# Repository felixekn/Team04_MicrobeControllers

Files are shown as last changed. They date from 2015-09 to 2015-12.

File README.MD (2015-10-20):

# Goal
A device capable of quickly measuring the OD600 of a culture tube

# Specifications
-  OD600 Range of 0.05-0.5
-  OD600 precision  of <0.02
-  Option: Functions with tubes with gradations
-  Tube to tube variability <0.02
-  Does not need to be portable, can utilize an outlet
-  Capable of measureing 1-100 samples in >15 minutes
-  Capable of being blanked against different media
-  Reads out at least 2 significant figures
-  Robust to rough handeling by user

# Checkpoints
-  Select a photodetector
-  Select a light source
-  Select splitter
-  Interface with photodetector
-  Intereface with light source
-  Determine performance parameters of system and if they meet our specifications
-  Design a user interaction method
-  Select parts for user interaction
-  Interface with parts for user interaction
-  Design chasis and wiring
-  Produce chasis and wiring
-  Code complete system
-  Analyze performance
  
#Project Title: 
**Rapid Optical Density Detector (RODD)**

#Rough Project Description
Develop a small optical density (OD) measuring device that can either sit in or near an incubator for the purpose of rapidly reading the OD600 of culture tubes containing bacteria to determine their growth phase.

#Project Abstract:
A ubiquitous synthetic biology protocol is to grow liquid cultures of cells in 14mL culture tubes within a large orbital shaker incubator to a desired optical density (OD) for various experimental reasons. The challenging and at times frustrating aspect of this protocol is quantifying when the cells have reached their desired density. Traditionally, researchers either pipette samples into cuvettes and read these on a large spectrophotometer or hold each culture tube up to a light source and estimate OD based on experience. The first approach does not scale well with increasing culture tubes while the latter approach is susceptible to large errors especially at low ODs (<0.1 OD 600nm). A solution to this problem is to develop a device that sits within or on the orbital incubator that can read the OD of liquid cultures while they're within their culture tubes. By using Beer's law, an Arduino, a couple of photo detectors, and a laser, the proposed OD measuring device will be able to accurately (+/- 0.1 OD 600nm) and rapidly read out culture tube OD for the purpose of quickly quantifying if a liquid cell culture has reached its desired OD.

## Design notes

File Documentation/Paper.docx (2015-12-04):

A Low Cost Culture Tube Spectrophotometer

BIOE521 - 12/3/2015 - Felix Ekness, Brian Landry

Abstract

A ubiquitous synthetic biology protocol is to grow liquid cultures of cells in 14mL culture tubes within a large orbital shaker incubator to a desired optical density (OD) for various experimental reasons. The challenging and at times frustrating aspect of this protocol is quantifying when the cells have reached their desired density. Traditionally, researchers either pipette samples into cuvettes and read these on a expensive spectrophotometer or hold each culture tube up to a light source and estimate OD based on experience. The first approach is expensive and does not scale well with increasing culture tubes while the latter approach is susceptible to large errors especially at low ODs (<0.1 OD 600nm). We have solved this problem with the development of a compact and cheap spectrophotometer named the Rapid Optical Density Detector (RODD) that can measure OD through the culture tubes. RODD uses the Beer-Lambert law, an Arduino Uno, a single light-to-frequency converter, and a 600nm LED, a four segment LED display, a push button, and a 3D printed enclosure to cheaply and rapidly measure the OD of liquid cultures within 14mL culture tubes with a resolution of +/- 0.01 OD.

Background and Significance

In synthetic biology laboratories, measuring and tracking the density of cells within liquid cultures is paramount to nearly all in vivo experiments. As bacteria grow in liquid media, they consume nutrients and increase in density. During growth, the available nutrients decrease, resulting in phenotypic changes that affect experimental outputs. Thus it is crucial for experiments to end at the same cell density to avoid phenotypic changes, such as variations in DNA replication speed. To measure cell density within standard 14mL liquid culture tubes, two techniques are used: measuring the absorbance of the culture using a spectrophotometer or measuring absorbance through eyeballing.

Spectrophotometers measure the absorbance of a 600nm laser through a 1cm path of the liquid culture. This measurement is known as the optical density (OD) at 600nm (OD600) and is a standard proxy for microbial cell density. Spectrophotometers have been around for decades and although they are ubiquitous in laboratories, they are costly to purchase ($500-2000 used on Ebay and >$5000 new from VWR [1,2]), bulky, and require samples be placed into expensive ($1/per), non reusable cuvettes. Their high cost limits labs to usually one spectrophotometer and the requirement of pipetting samples into cuvettes becomes financially and time costly for >10 samples as well as perturbs the growth of the liquid cultures being measured. While there have been attempts to make cheap spectrophotometers, they have been impractical for laboratory environments or use the same time intensive and costly cuvettes [3,4].

The other technique of measuring liquid culture OD is through eyeballing the liquid culture within its culture tube against a light source. This technique requires experience but is cheap, quick, and does not perturb the growth environment of the cultures. Measuring OD with this method is prefered for >10 samples but is known to be highly inaccurate even for the most experienced researcher. Thus a cheap, quick to use, and accurate spectrophotometer is needed to enable synthetic biologists to rapidly and precisely measure OD of large quantities of experimental liquid culture tubes without perturbing the growth environment of the cells.

Design and Development

Below are the specifications for our spectrophotometer named Rapid Optical Density Detector (RODD):

Property | Specification | Achieved Value
Measurement Range | 0.05-0.5 OD600 | 0.05-1.0 OD600
Precision | <0.02 OD600 | +/- 0.01 OD600
Portability | Can be located next to an incubator but can still use a wall outlet for power | Achieved specification
Measurement rate | > 10 Samples/minute | 30 samples/minute
Visual Readout | Contains at least 2 significant figures | Contains 3 significant figures and a sign
Durability | Capable of being roughly handled and occasionally dropped | Survived testing and simulated dropping
Ease of use | Requires minimal interaction and promotes quick use | A single button press activates the machine which then has continual readout to the user
Cost | <$50 | Button = $0.5 Arduino Uno = $24.95 600nm LED = $0.35 Light-to-frequency-converter = $3.56 LED Display = $16.95 3D printed Housing = negligible Total = $46.31

User interface design

We approached our user interface with the goal of it being simple and quick to use. This meant limiting user interaction and achieving quick feedback to the user of the predicted OD600 of the culture. We first specified the four usage modes of the device:

1. Turned on
2. Measuring the blank
3. Measuring a sample
4. Turned off

Our first design decision was to condense the user input required to transition from the 4th state to the 1st and then 2nd states to a single button press, which both turns on the device, activating the numeric display, as well as initiates the blanking procedure. To further simplify usage we then automated transition from measuring the blank to measuring a sample to occur after one second of measuring the blank. While the device is measuring the sample it displays a one second running average of the OD600 reading. This real time display speeds up feedback to the user of the measured OD600 of the culture, decreasing the time required to quantify the density of the culture. It additionally removes the need for the user to signal the RODD each time a new sample is being measured, instead the user simply inserts the new sample and waits for the reading to stabilize after one second. Lastly, we created an automated turn off of the RODD after 10 minutes, both negating the need for the user to turn it off as well as removing the possibility of it accidentally being left on for long periods of time. A summary of the designed workflow is depicted in the flowchart below.

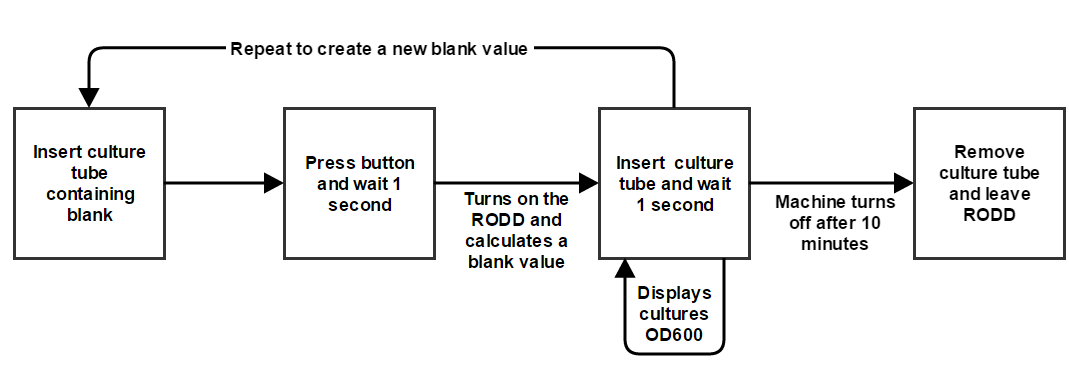
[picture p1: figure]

Figure 1: RODD user workflow flowchart

Spectrophotometer part selection

Part selection for RODD focused on attaining a high signal to noise ratio with relatively cheap parts. This lead to initially choosing a light-to-frequency-converter (LTFC) (part TSL237) that linearly converts input light intensity to an output square wave frequency over 5 logs of light intensity and an economical red laser (VLM-635/650-03 Series) with a wavelength of 635-650nm and beam diameter of 6+/-1 mm. After wiring these to an Arduino Uno and placing them within our custom 3D printed housing (see Figure 2A), it was observed that slight tilting of the culture tube dramatically changed the output of the LTFC. This was due to the laser’s focused beam and how the beam traveled through the culture tube. A slight change in the angle of entry into the culture tube resulted in a refraction large enough to shift the focus of the beam away from the center of the LTFC. This resulted in large OD600 variability from tube to tube which caused the noise of the system to surpass the signal. To fix this issue, the laser was swapped out for a less powerful but wider beam diameter LED. Since the LED’s beam diameter entering the culture tube is much larger than the laser’s, the effect of the refraction was predicted to be much less since the main focus of the LED beam should still hit the LTFC after refraction (see Figure 2B). Upon testing this hypothesis, the signal to noise ration was greatly increased with the LED OD600 light source configuration and thus RODD uses an LED instead of laser OD600 light source.

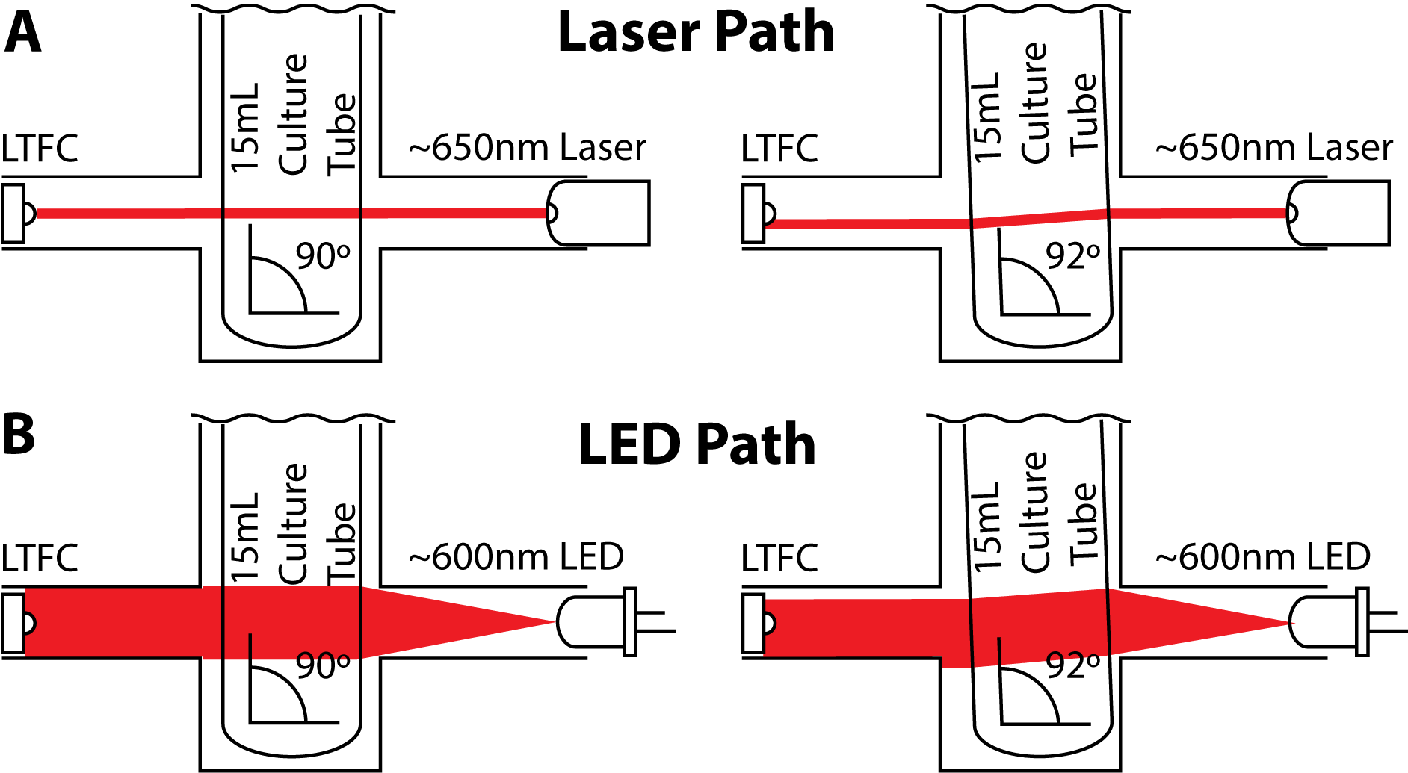
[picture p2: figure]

Figure 2: Beam path deviation of OD light source due to refraction when culture tube is tilted by 2º

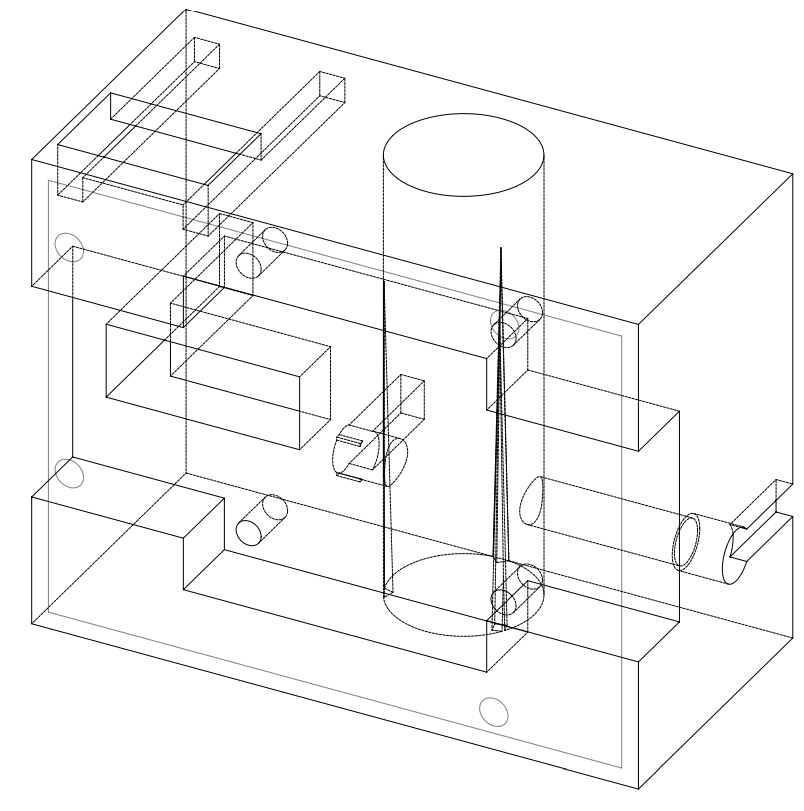
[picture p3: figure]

Design of casing

Figure 3: Diagram of the custom 3D printed housing that RODD uses.

When considering the selection of materials and organization of the physical parts of the RODD we took into expected levels of handling, our prior knowledge as well as the various fabrication technologies we had access to. We choose to 3D print over technologies such as laser cutting to create the casing for the RODD because it enabled the creation of various enclosed wiring paths. This resulted in compartmentalized wiring hidden from the user which we hope will make the connections more durable. We also had previous experience creating and printing models and had access to a 3D printer in our lab. The final model which was printed is shown below.

During testing of prototypes of our device we found that the angle of the culture tube greatly influenced measured absorbance, particularly when used with a laser (see Figure 2). Although the light source was changed to an LED to fix this issue, we also redesigned the culture tube holder to have a tighter fit. We used three triangular protrusions placed on the sides of the tube holder which decreased the relative diameter of the holder from the entry to the bottom of the holder (Figure 3). These protrusions in addition to the use of an LED light source eliminated previously identified noise generated from the vertical angle of the culture tube within its holder.

Coding

The RODD was programmed in the Arduino Programming Language using the standard arduino sketch format. The core of the program is contained in a loop which updates the state of the device at a set interval. The loop checks for changes in the state of the button, and then begins countdowns to both end the blanking of the device (measures light intensity through a culture with no cells which is a proxy for input light source) after one second and operation of the device after 10 minutes. It then records experimental measurements from the LTFC, computes the OD600 through the Beer-Lambert law, and displays the computed output on a four segment LED screen.

An important feature of this design was to create a responsive system while also supporting continuous integration from the synchronous photodetector. The original design queried the photodetector for a measurement over a one second time period. However, this locked the system for the entire second, making both the button and LED unresponsive during this period. To accommodate this while still calculating a one second average from the photodetector we created a continuously updated buffer which stored the last ten measurements from the photodetector. The LTFC was then queried ten times a second for a 100 millisecond period and these values were stored in the buffer. This permitted updates of the LED and button state every 100ms creating a much more responsive system. Additionally, it enabled the display of a continuously updating one second running average OD600 value to the user.

Quantification and Qualification

Calibration Technique

RODD was calibrated to display OD600 using 10 serially diluted titanium dioxide colloid solutions (suspended in water). These solutions were first read on our lab’s commercial spectrophotometer within 1mL cuvettes (Table 2, column 1). Then these solutions were measured within 14mL culture tubes at a volume of 4mL within RODD (Table 2, column 2). With both of these measurements, a first order polynomial was fitted to the spectrophotometer and RODD readings to create a mapping between spectrophotometer OD600 and RODD absorbance. This mapping was then hard coded into the core code that calculates RODD OD. The standard titanium dioxide solutions were then remeasured with the now calibrated RODD, yielding OD600 values +/-0.01 away from the spectrophotometer OD600 measurements of the same standard solutions (Table 2, column 3).

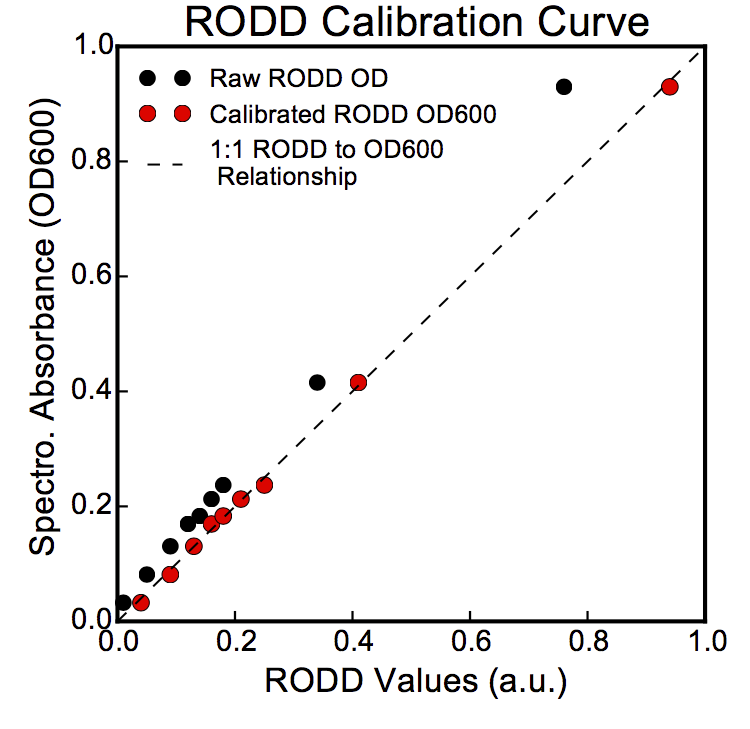
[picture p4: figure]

Spectrophotometer OD600 | Raw RODD OD | Calibrated RODD OD600
0.0325 | 0.01 | 0.04
0.08145 | 0.05 | 0.09
0.13062 | 0.09 | 0.13
0.16941 | 0.12 | 0.16
0.18323 | 0.14 | 0.18
0.21266 | 0.16 | 0.21
0.23708 | 0.18 | 0.25
0.41538 | 0.34 | 0.41
0.92972 | 0.76 | 0.94

Table 2: Spectrophotometer and RODD OD readings of 10 serially diluted titanium dioxide colloid solutions.

Figure 4: Plot of the values located in Table 2. The 1:1 RODD to OD600 relationship is the ideal relationship between the OD600 values RODD reads and what the spectrophotometer outputs

Deployment

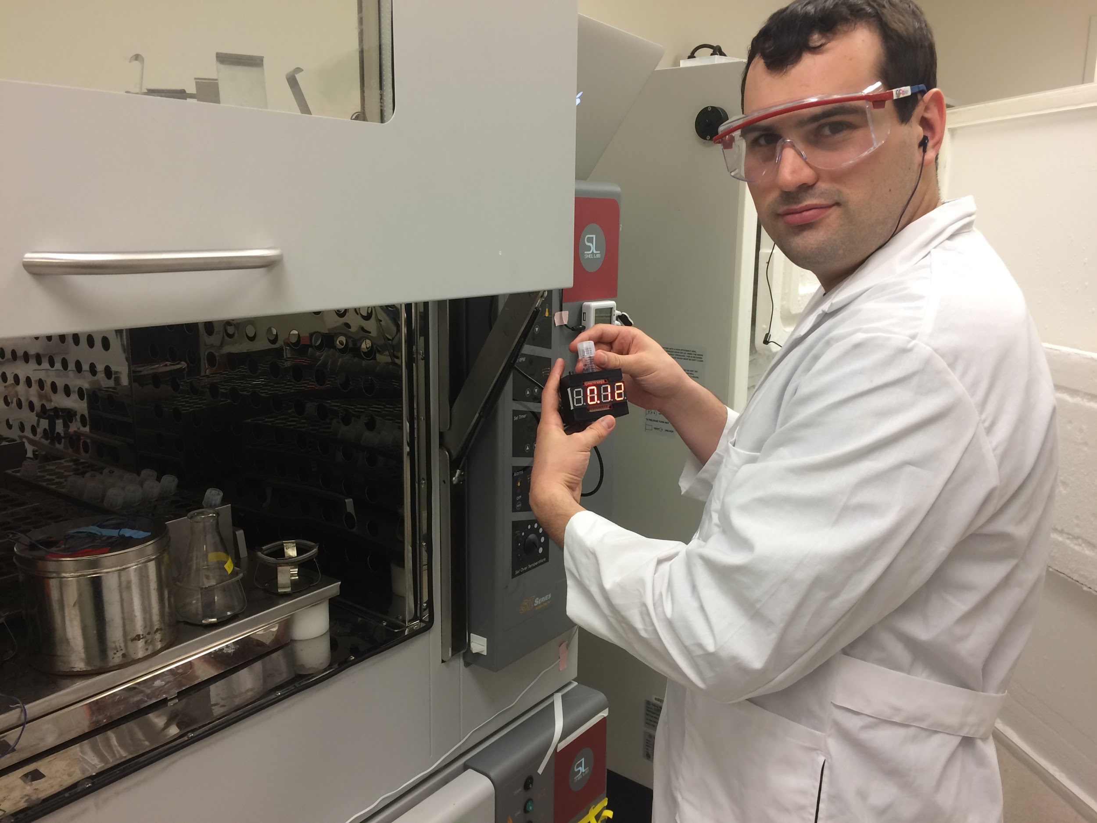
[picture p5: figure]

The extensive prototyping accomplished in this project has led to a device that is ready for preliminary deployment in our lab environment. We have begun to use the RODD to measure the OD600 of cultures in our incubator in the Tabor Lab (see image below). However there are several additional improvements which we are interested in examining. Primarily we would like to extend our 3D enclosure to cover the Arduino in addition to our electrical components. We expect this will increase the hardiness of the RODD and lead to a better user experiences. We are also interested in adding a web based storage system for the OD600 measurements from the device. We envision a system where the user presses the button after inserting each culture, which records the current reading to a spreadsheet that can subsequently be access via the internet. We look forward to adding these improvements to the RODD and demonstrating its long term performance in the Tabor Lab.

Figure 5: RODD in action

Citations

[1] Ebay. Search Term: “Spectrophotometer.” http://www.ebay.com/bhp/spectrophotometer

[2] VWR. Product Category: “Spectrometers.”

https://us.vwr.com/store/search?label=&vpc=&pimId=597202

[3] D. R. Albert, M. A. Todt, H. F. Davis. “A Low-Cost Quantitative Absorption

Spectrophotometer.” J. Chem. Educ. 2012, 89, 1432-1435.

[4] Dusjagr. “Optical Density Sensor aka Kafi-Schnapps Detektor.” Makerbot Thingiverse. Apr

15, 2013. http://www.thingiverse.com/thing:74415

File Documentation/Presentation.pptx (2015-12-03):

## The RODD: A Low Cost Culture Tube Spectrophotometer

- Brian Landry, Felix Ekness

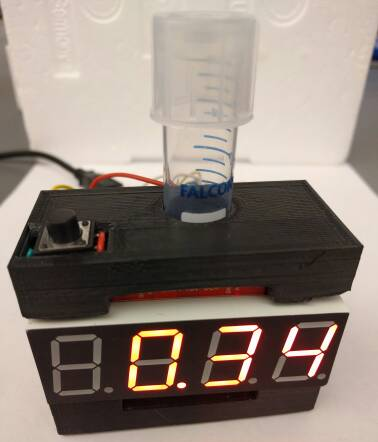
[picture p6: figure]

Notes: Felix

## Counting Bacteria in a Culture Tube

- Cannot monitor density of bacteria in standard culture tube
  - Volume required to use spectrophotometer is too much
  - Tube doesn’t work with spectrophotometer

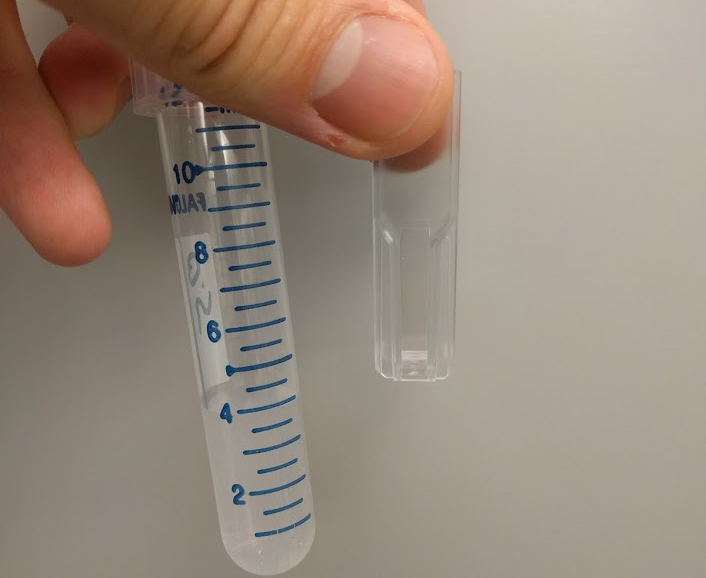
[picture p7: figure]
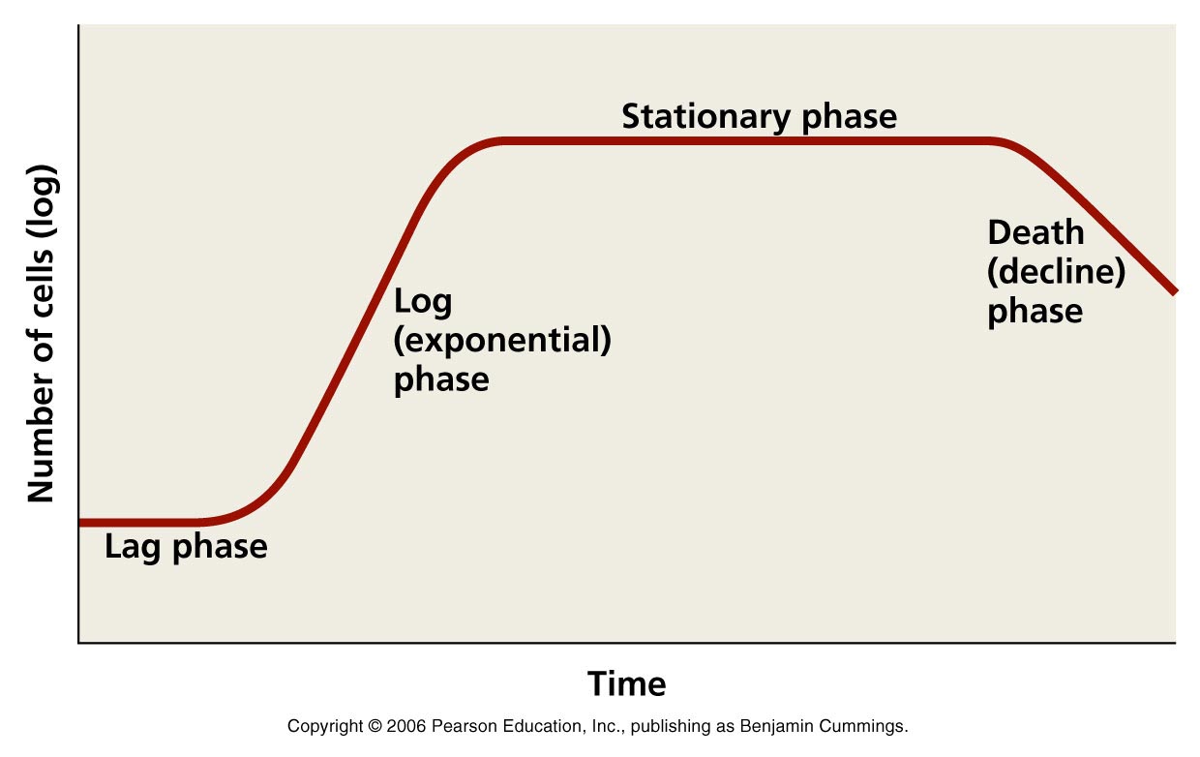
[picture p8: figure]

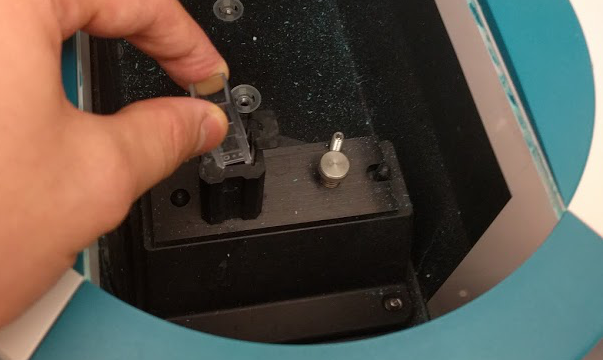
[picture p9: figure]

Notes: Felix

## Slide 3

Counting Bacteria in a Culture Tube

- Cannot monitor density of bacteria in standard culture tube
  - Volume required to use spectrophotometer is too much
  - Tube doesn’t work with spectrophotometer

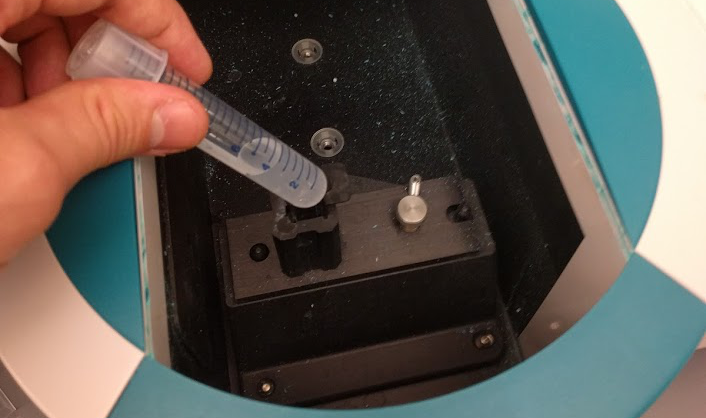
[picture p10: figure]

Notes: Felix

## Proposed Solution: The RODD

- A Rapid Optical Density Detector (RODD)
- A mini spectrophotometer which will sit next to a lab incubator to monitor many bacterial cultures simultaneously
- Should be easy, quick and intuitive to use
- Needs to be precise enough to allow us to experiment on bacteria in correct growth range

Property | Specification
Measurement Range | 0.05-0.5 OD600
Precision | <0.02 OD600
Portability | Can be located next to an incubator but can still use a wall outlet for power
Measurement rate | > 10 Samples/minute
Visual Readout | Contains at least 2 significant figures
Durability | Capable of being roughly handled and occasionally dropped
Ease of use | Requires minimal interaction and promotes quick use
Cost | <$50

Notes: Felix

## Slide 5

Property | Specification
Portability | Can be located next to an incubator but can still use a wall outlet for power
Measurement rate | > 10 Samples/minute
Visual Readout | Contains at least 2 significant figures
Durability | Capable of being roughly handled and occasionally dropped
Ease of use | Requires minimal interaction and promotes quick use

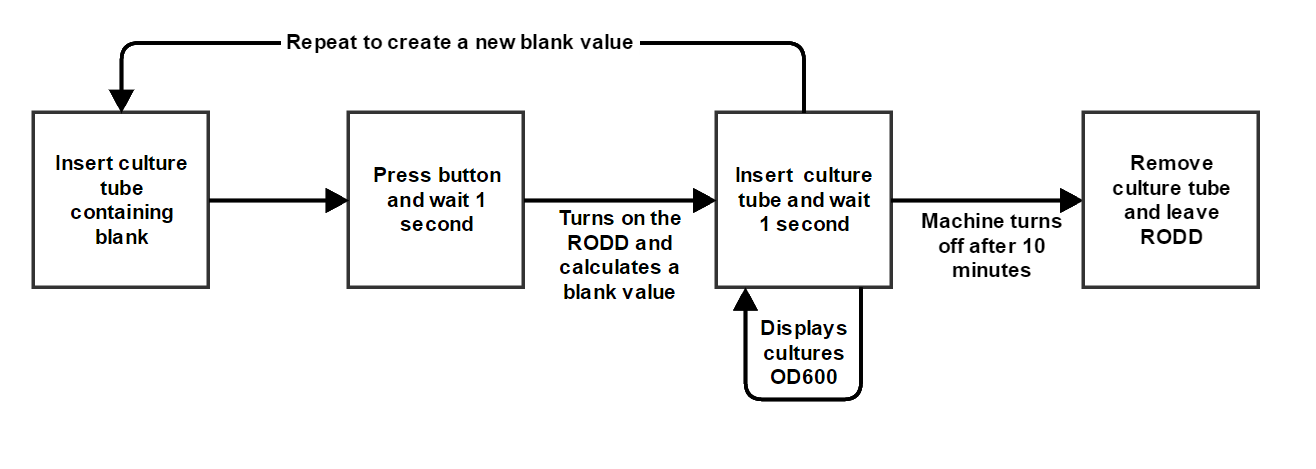
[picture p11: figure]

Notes: Brian

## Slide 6

Photodetector: large linear range to provide high precision and accuracy

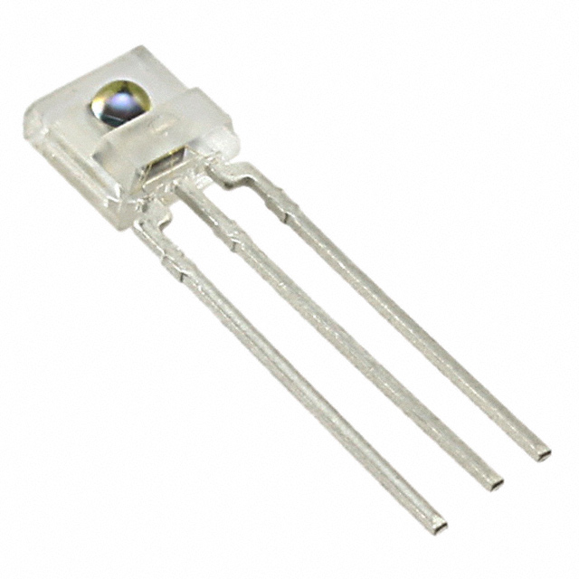
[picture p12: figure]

650nm laser for a bright concentrated light source

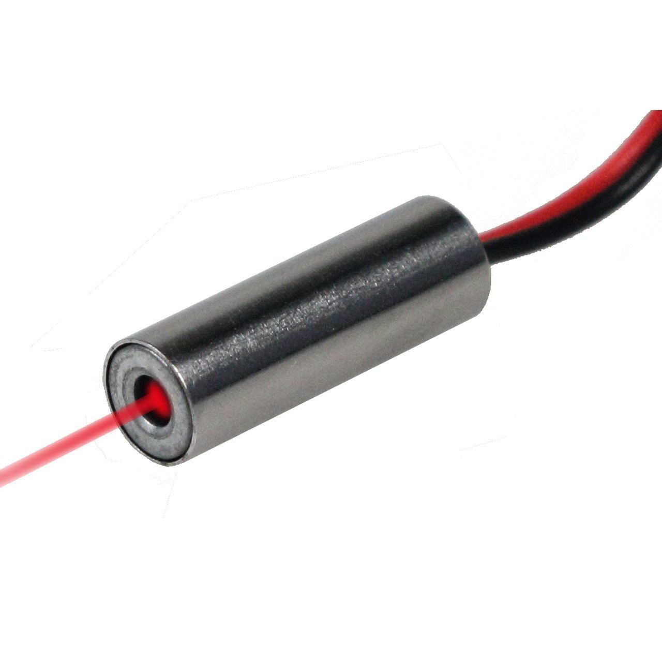
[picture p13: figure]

Single large button for user input

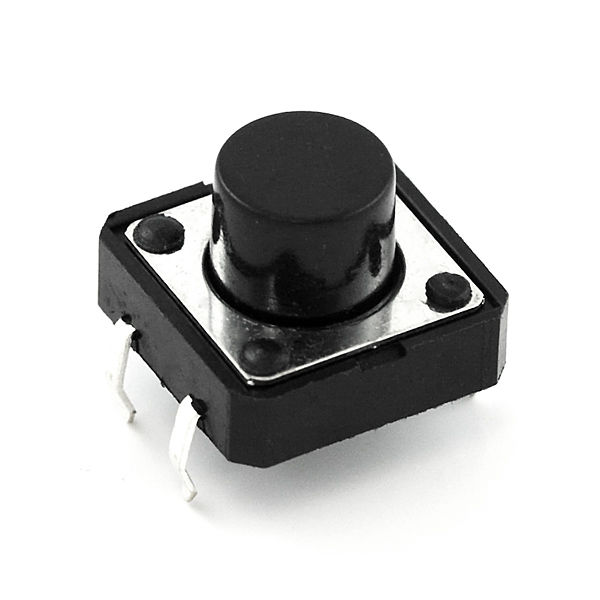
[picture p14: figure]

Four digit seven segment display capable of displaying three signed digits

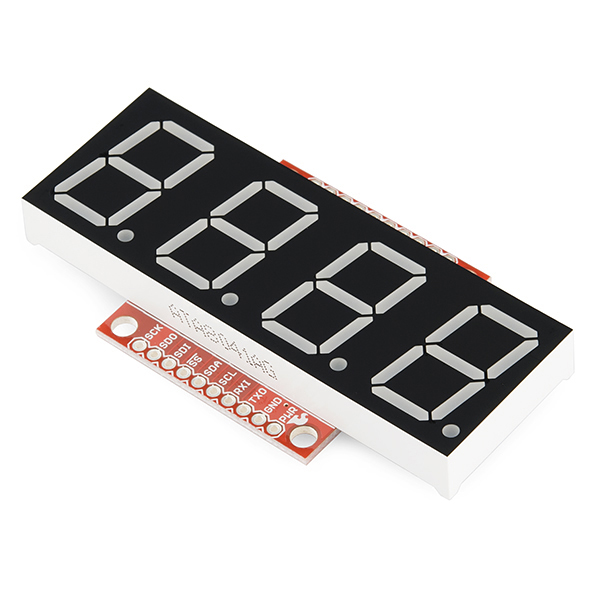
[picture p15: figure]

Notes: Brian

## Construction of the RODD

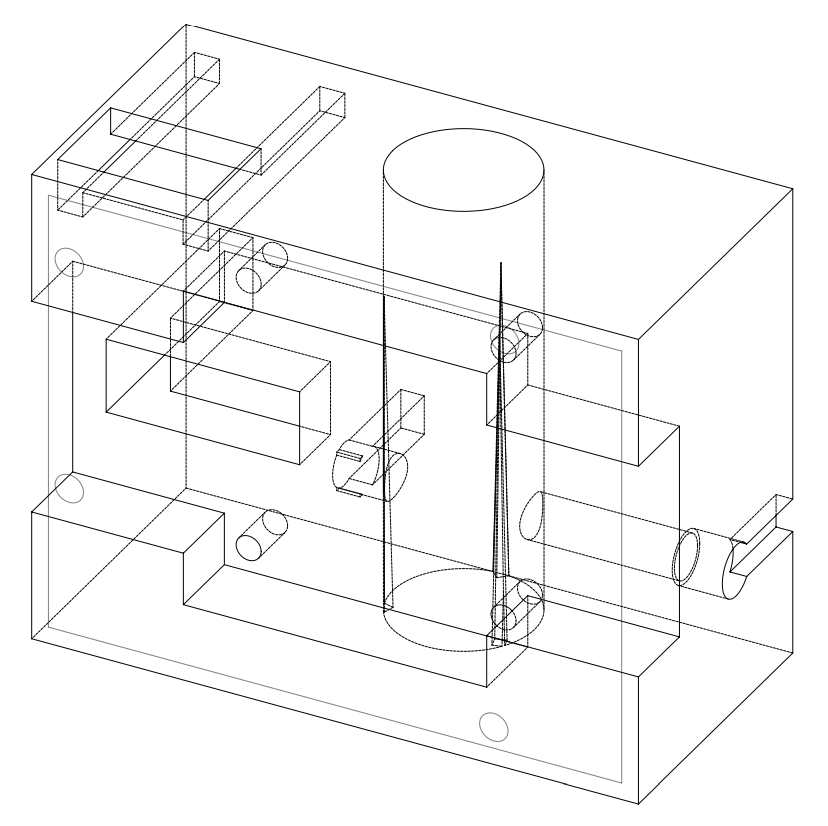
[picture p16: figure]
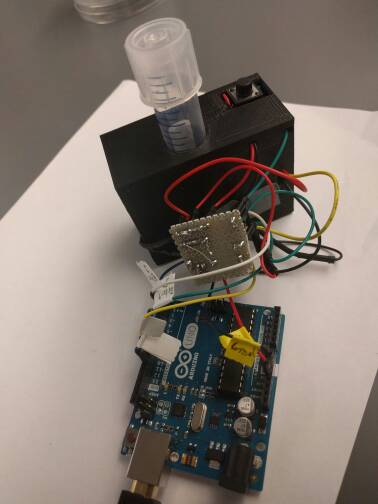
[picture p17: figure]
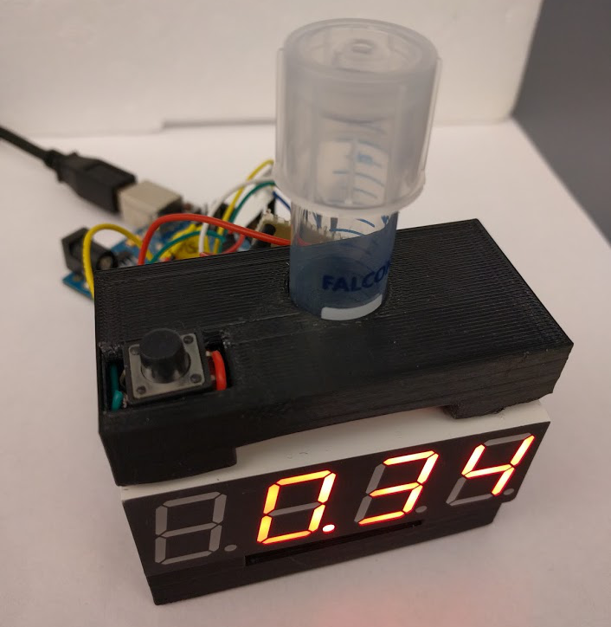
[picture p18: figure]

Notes: Brian

## Engineering Challenge: A responsive program

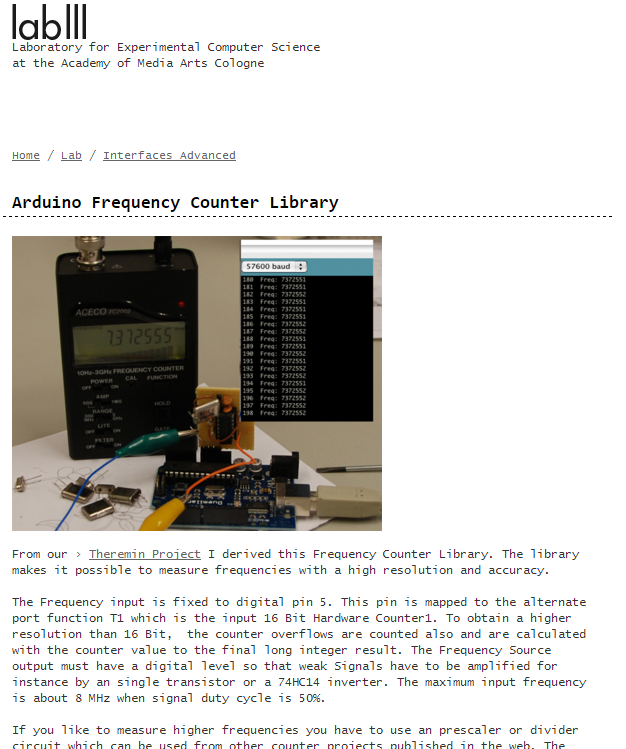
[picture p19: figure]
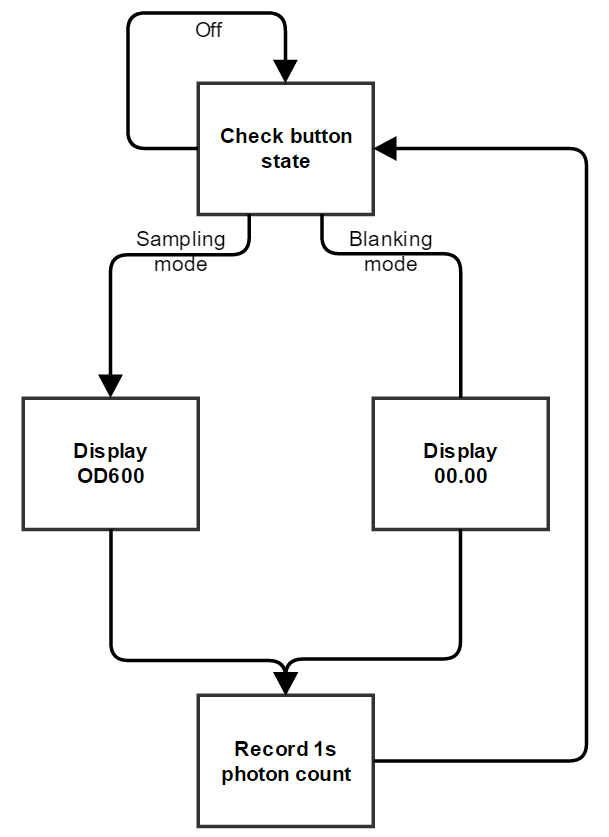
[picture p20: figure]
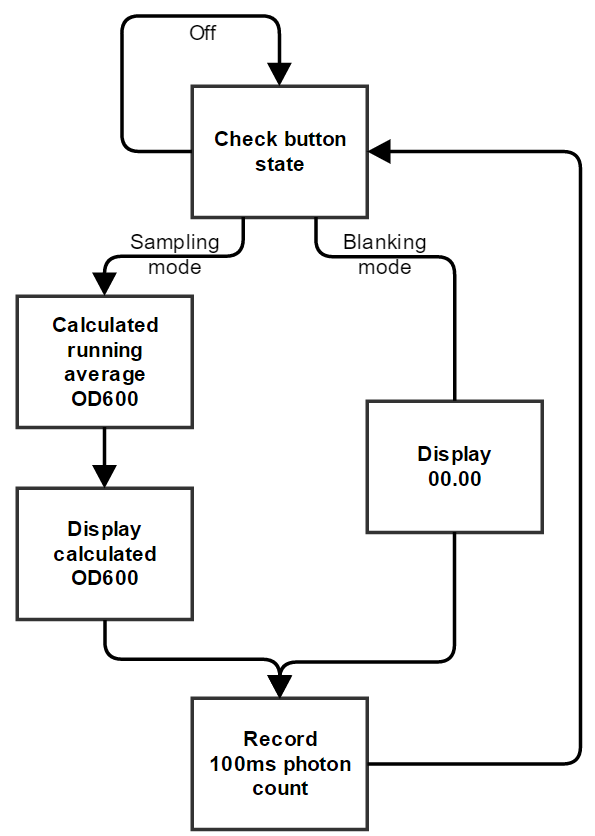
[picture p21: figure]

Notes: Brian

## Engineering Challenge: A responsive program

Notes: Brian

## Engineering Challenge: Laser deflection

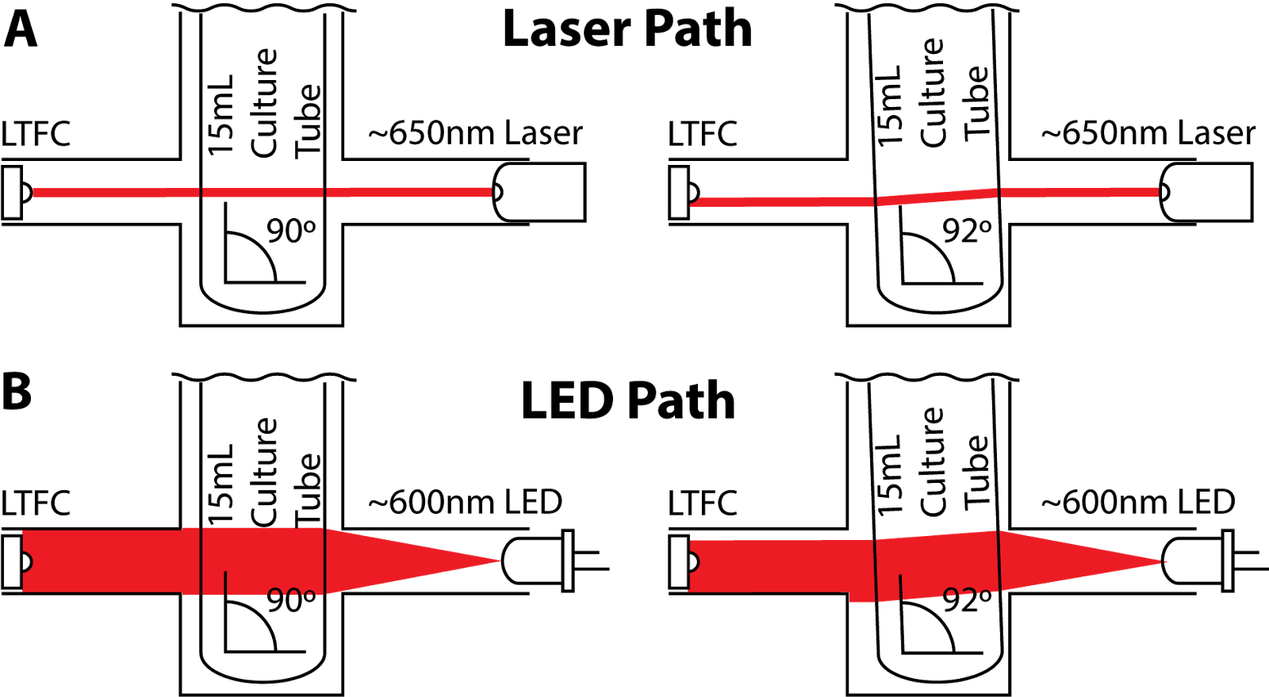
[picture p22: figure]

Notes: Felix

## Performance Analysis

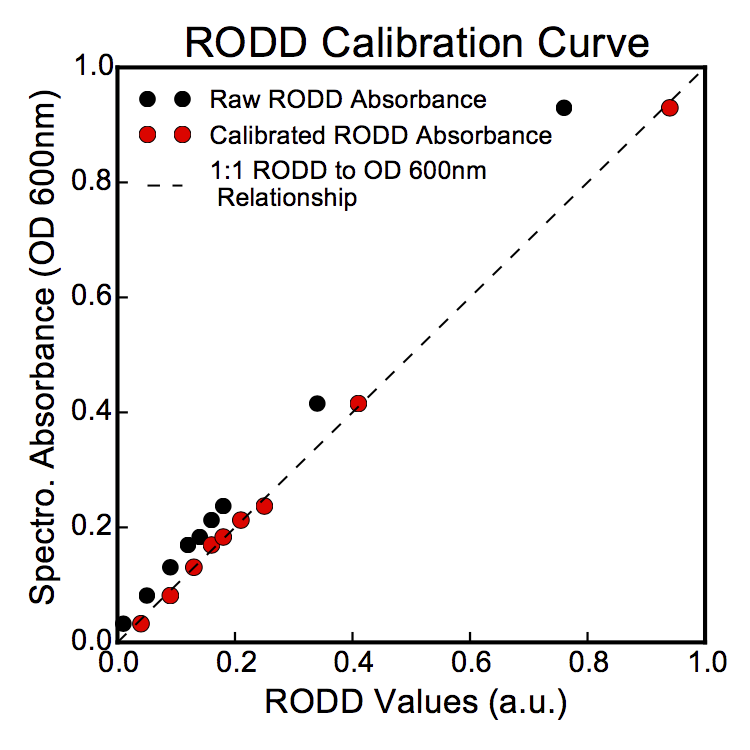
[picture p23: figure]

Property | Specification | Achieved Value
Measurement Range | 0.05-0.5 OD600 | 0.05-1.0 OD600
Precision | <0.02 OD600 | +/- 0.01 OD600
Portability | Can be located next to an incubator but can still use a wall outlet for power | Achieved specification
Measurement rate | > 10 Samples/minute | 30 samples/minute
Visual Readout | Contains at least 2 significant figures | Contains 3 significant figures and a sign
Durability | Capable of being roughly handled and occasionally dropped | Survived testing and simulated dropping
Ease of use | Requires minimal interaction and promotes quick use | A single button press activates the machine which then has continual readout to the user
Cost | <$50 | Total = $46.31

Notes: Felix

## Documentation and Deployment

- Report, code, 3D models and parts are available via github
- Well annotated code and structured code
- Began trial usage in lab
- Future work
  - Fully enclosed Arduino
  - Raspberry pi connected cloud storage of OD600 measurements

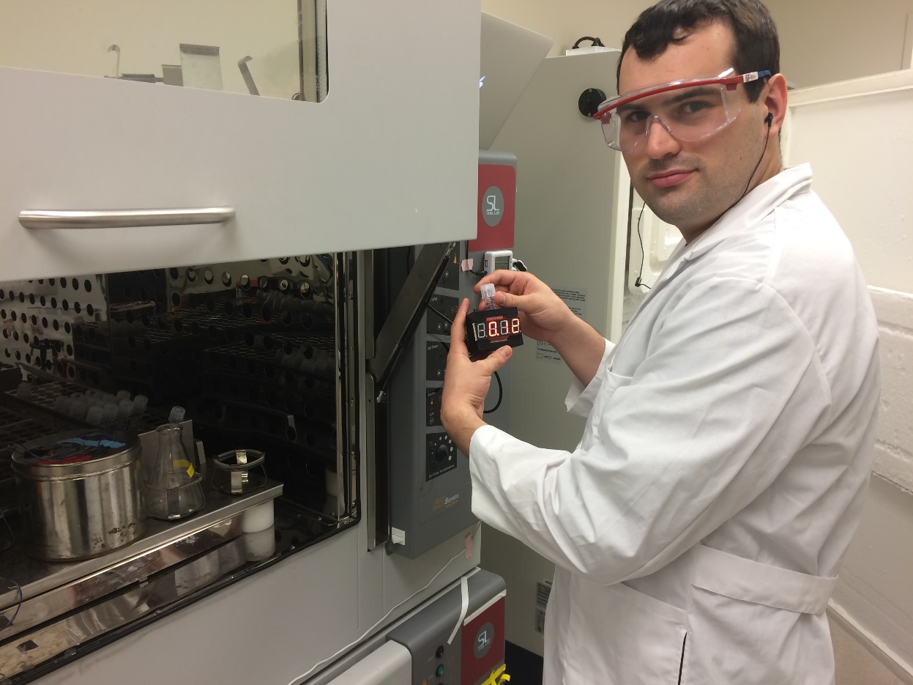
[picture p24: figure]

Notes: Felix

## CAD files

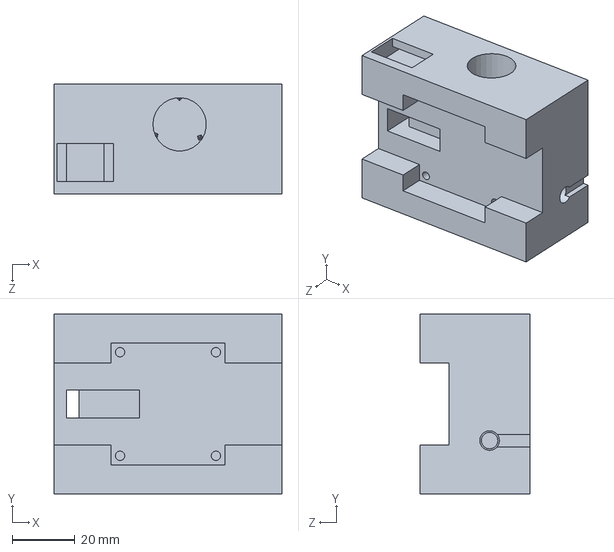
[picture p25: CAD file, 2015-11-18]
Solidworks/Casing.SLDPRT
72.6 x 57.3 x 35.0 mm

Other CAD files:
Solidworks/Casing.STL

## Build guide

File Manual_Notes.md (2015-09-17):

# Team04_MicrobeControllers
# Brian Landry, Felix Ekness

### man
Use to get the help manual for different commands with format: ``` man command```
### who
Lists all of the system user variables.  
Use ```who -u``` to determine the username
### whoami
Displays the current user
### hostname
Use ```hostname --short``` to display short hostname
Use ```hostname -i``` to display the IP address
### pwd
Print the current working directory
### uptime
Displays the amount of time the Pi has been on
### python
Use ```python --version``` to determine python version
### ping
Use ```ping url``` to ping a website
### whereis
Use to display the location of a command, such as ```whereis man```
### which
Locates a command on the disk
### cat
Opens a short text file, example: ```cat /proc/cpuinfo```
### raspistill
Controls the raspberry's camera
### crontab
Used to schedule the firig of commands perodically
http://kvz.io/blog/2007/07/29/schedule-tasks-on-linux-using-crontab/
### top
displays currently active commands and their resource usage

### Restart and Shutdown
sudo shutdown -r now -> restarts
sudo shutdown now -> shutsdown pi
---------------------------------------------------------------------------------------------------------
# Lab 2 Notes
### echo
Prints what was written in the command line after submission
### cat
prints out contents of file as well as concatinates files, strings, variables, etc
### wc
Prints out total number of words (-w) or total number of characters in bites (-c)
### >
creates new file or rewrites selected file
e.g. echo "Hello world!" > hi.txt
### >>
Creates file from echo if file does not yet exist, appends if file exists
### ls -la
gives file infromation in bites, prints hidden files/non text files
### head and tail
prints either the first 10 or last line 10, respectively, of a file
-[1-10] prints the 1st, 2nd, 3rd...10th line of head or last
-1 = first line, -3 = third lien
### more
prints contents of file to fill screen and allows for scrolling to additional lines of the file using the arrow keys
### |
suppresses data stream (does not print to screen) but allows functions to act on the stream.
Example: more hi.txt | grep hi  returns all instances containing the characters "hi"
### grep
find
### -n
prints line number
### wget
access a website
#### -q
quietes output of wget
#### -qO-
prevents from saving to a disk
### tee
Outputs standard output and writes result to a file
e.g. ifconfi | cat -n | grep "inet addr" | tee specific_line_in_ifconfi.txt
### cp
Copies from a file to a new file
e.g. cp hi.txt new_file.txt
### id -u
Prints user specific information
### nano
onboard text editor
### raspistill
activates camera
-o output filename
-v verbose output: gives you detailed information on photo captured
### opt-get
the downloader or package manager for linux
### fbi
image viewer
e.g. fbi smile.jpg
-a autozoom
-d framebuffer of device
-vf vertical flip
-hf horizontal flip
-v be verbose, status line on bottom of prompt
-noverbose
-t time in secomds (e.g. -t 1 equates to a picture per second slide show on repeat)
### raspivid
takes video with camera
-o specifies output file
### omxplayer
video player
-o specifies out type (e.g. hdmi)
### 2>&1
pipes standard error (stderr) to standards output (stdout)  

------------------------------------------------------------------------------------------------------------
# Lab 3
### CHMOD
```
CHMOD +x filename
````
Use this command to make a file execuable

### grep

global regular expression print

Searchs an input file for a string and prints lines which match it
````
grep string filepath
````

-n Shows line numbers  
-v Gives negative results instead of positive results  
-vn Gives negative results and line numbers  
-c only prints number of lines matched  
-l only prints filesnames of files which contain the string  
-i ignores case when searching  
-x Searchs for exact matches only
-A# Display additional lines following the line in which the match was made

####REGEXP
You can include regular expressions in your grep queries  
-E also use of extended regexp commands  
$ is end of line  
? matchs 1 or 0 occurences of the previous character  
| seperates two search strings with or functionality, eg. string1|string2  
\ escapes a special character allowing it to be searched for. Use 'single quotes' when using this character.

###AWK
A text pattern scanning and processing language. read here fo rmore info http://www-users.york.ac.uk/~mijp1/teaching/2nd_year_Comp_Lab/guides/grep_awk_sed.pdf
````
BEGIN { b&. initialization awk commands b&}
{ b&. awk commands for each line of the fileb&}
END { b&. finalization awk commands b&}
````
Example which prints every third file using a for loop and getline to iterate  
````
ls -l | awk '{for (i=1;i<3;i++) {getline}; print NR,$0}'
````
Uses the following control statements:
-  if (condition) statement [ else statement ]
-  while (condition) statement
-  do statement while (condition)
-  for (expr1; expr2; expr3) statement
-  for (var in array) statement
-  break
-  continue
-  exit [ expression ]
-  
Example, find PMIDs from PubMed records:
````
awk '{if($1=="PMID-"){print $2}}' tsien.txt > tsien_PMIDs.txt
````
---------------------------------------------------------------------------------------------------------
# Lab 4 notes
### passwd
changes password for pi - must first renter old password then will take new password
### id
lists all user id's in the following form:  
uid=1000(pi) gid=1000(pi) groups=1000(pi)...  
uid = user id in integer with actual text in paretheses  
gid = group id
### apropos
searchers all manuel pages (grep for man)  
example: apropos user -> finds all man pages (liens of pages) with the word user in them
### addgroup
requires root, adds user to specified group  
addgroup <group name>
### adduser
requires root, adds new user  
adduser <user> <group name>  
note: to update user info, need to type $exit and then login to newly created user
### userdel
requires root, deletes a user  
userdel <user name>
### killall
force quits all processes of given name or all except killall  
example: killall python -> kills all python instances
## Python codes
### #! /usr/bin/python
added to the top of a python script, will idicate to the bash interpreter where to find the python interpreter to run the python script
### chmod +x python-dot.py
will make python-dot.py executable by the bash terminal  
e.g. ./python-dot.py
### Python: import re
use re to search for strings of given length:  
e.g. re.search(r".....", string1) will evaluate as either true or false for if string1 is of length 5 (true) or not (false)
### Python: import sys
sys.argv -> takes all options passed to the bash interpreter and stores them in a list  
e.g. $python ./python-dot.py 'hello world!!'  
with the python-dot.py containing the following lines:  

    sys.argv 
    print(arg)

will print ['./python-dot.py', 'hellow world!!']
# End of python codes
### crontab
type the following into the crontab -e file  
    * * * * *  command to execute
exicutes the command at m h  dom mon dow   command
### scp
copies files between hosts on a network. It uses ssh(1) for data transfer, and uses the same authentication and provides the same security as ssh(1)  
e.g. scp file user@IPaddress[directory]

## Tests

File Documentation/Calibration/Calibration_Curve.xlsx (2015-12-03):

 | RODD Readings (version 1 test housing 11/17/2015) |  |  |  |  |  |  |  |  |  |  |  | RODD Readings (Final housing_v1 11/19/2015)
 | LED | blank | 0.05 | 0.1 | 0.15 | 0.2 | 0.21 | 0.25 | 0.3 | 0.5 | 1 |  | blank | 0.05 | 0.1 | 0.15 | 0.2 | 0.21 | 0.25 | 0.3 | 0.5 | 1
 | 5348 | 10352 | 9419 | 8698 | 7327 | 6918 | 6839 | 6400 | 6185 | 4418 | 1867 | Raw Detector Units | 12401
 | 5356 | 10354 | 9420 | 8707 | 7347 | 6919 | 6838 | 6403 | 6163 | 4422 | 1866 | Raw OD | 0 | 0.01 | 0.05 | 0.09 | 0.12 | 0.14 | 0.16 | 0.18 | 0.34 | 0.76
 | 5385 | 10352 | 9419 | 8712 | 7321 | 6906 | 6837 | 6404 | 6164 | 4423 | 1866 | Mapped OD | 0 | 0.04 | 0.09 | 0.13 | 0.16 | 0.18 | 0.21 | 0.25 | 0.41 | 0.94
 | 5386 | 10350 | 9419 | 8716 | 7324 | 6904 | 6836 | 6405 | 6165 | 4424 | 1867
 | 5386 | 10348 | 9419 | 8715 | 7369 | 6901 | 6834 | 6407 | 6163 | 4423 | 1867 |  | RODD and Spec Readings (Final housing_v1 12/2/2015)
 | 5387 | 10353 | 9421 | 8715 | 7377 | 6902 | 6832 | 6407 | 6162 | 4440 | 1868 | Raw OD | 0 | 0.01 | 0.03 | 0.07 | 0.1 | 0.17 | 0.18 | 0.26 | 0.46 | 0.76
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

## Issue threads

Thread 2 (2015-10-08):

### ISSUE TITLE
Select a light source

### ISSUE THREAD

**Issue by BrianLandry** [felixekn/Team04_MicrobeControllers#2]

**Comment by felixekn** [comment]
http://www.digikey.com/product-search/en?KeyWords=VLM-650-03-LPA-ND&WT.z_header=search_go

**Comment by felixekn** [comment]
The laser's operating temp is 12-30ºC so if we use this laser, the OD detector can't be put into the incubator.

**Comment by BrianLandry** [comment]
Why aren't we using the lasers we are using in lab? And did you check to
see if we have any spares?

**Comment by felixekn** [comment]
These are the lasers that we have in lab and I checked and we do have some for us to use.

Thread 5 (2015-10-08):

### ISSUE TITLE
Select an LED interface

### ISSUE THREAD

**Issue by BrianLandry** [felixekn/Team04_MicrobeControllers#5]

**Comment by BrianLandry** [comment]
This is the current top option for an LED screen
https://www.sparkfun.com/products/11644

**Comment by felixekn** [comment]
Looks good. If for whatever reason we need a stripped down screen without its own microcontroller, we can buy this one:
http://www.digikey.com/product-detail/en/LDQ-M512RI/67-1440-ND/252634 http://www.digikey.com/product-detail/en/LDQ-M512RI/67-1440-ND/252634

-Felix

**Comment by BrianLandry** [comment]
Yeah I saw those on sparkfun, they are just much more of a pain to program.

**Comment by BrianLandry** [comment]
Connect via one of these https://www.sparkfun.com/products/9915?_ga=1.137509680.1693251387.1432681039

**Comment by felixekn** [comment]
What would we be connecting with this? The button?

**Comment by BrianLandry** [comment]
ordered

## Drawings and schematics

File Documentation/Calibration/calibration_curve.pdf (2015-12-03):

## RODD Calibration Curve

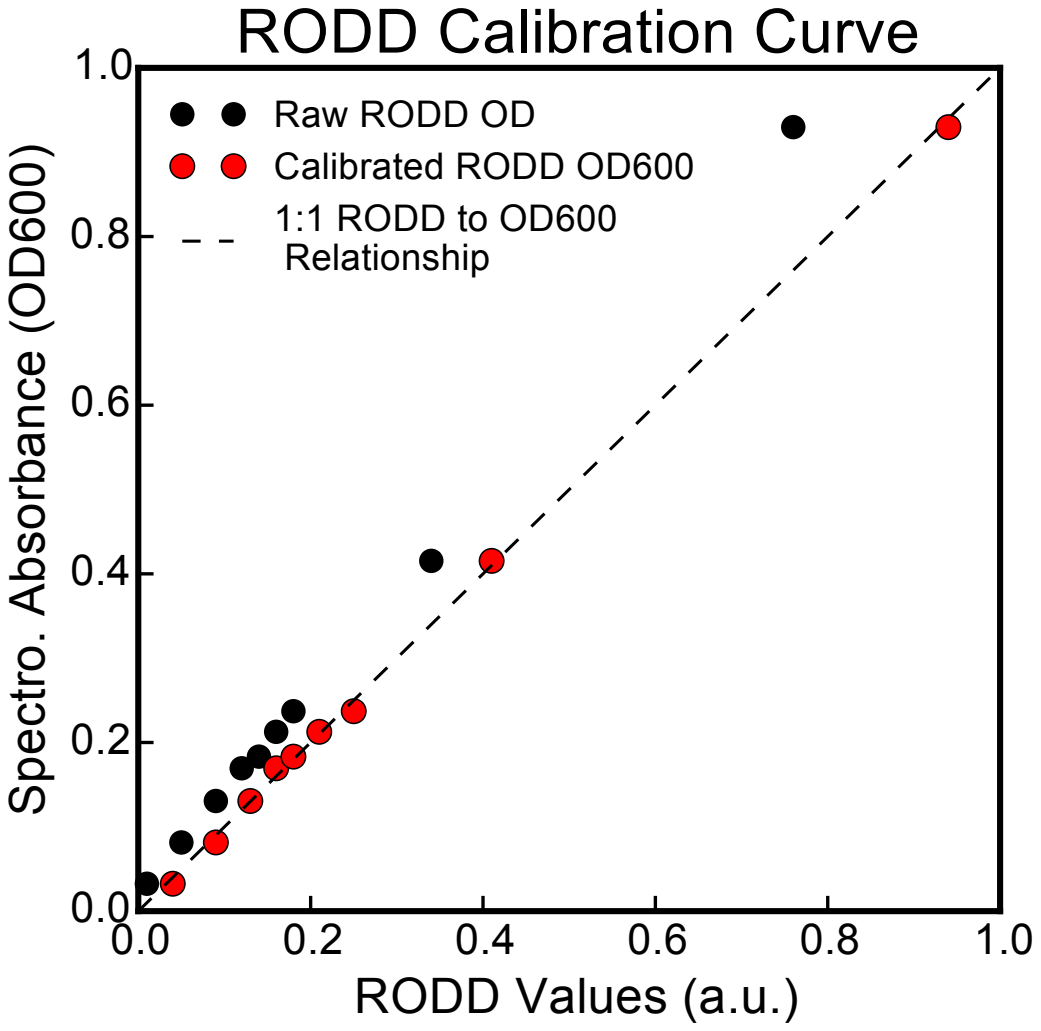
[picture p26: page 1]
RODD Values (a.u.); Spectro. Absorbance (OD600)

Raw RODD OD
Calibrated RODD OD600
1:1 RODD to OD600
Relationship

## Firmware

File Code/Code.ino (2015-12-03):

#include <math.h>
#include <SoftwareSerial.h>
#include <FreqCounter.h> //http://interface.khm.de/index.php/lab/interfaces-advanced/arduino-frequency-counter-library/

SoftwareSerial Serial7Segment(7, 9); //RX pin, TX pin for LED display

int LEDPin = 11;
int buttonPin = 2;
const long operationPeriod = 600000; //How long the device stays on [ms]
const long blankingPeriod = 1000;
const long integrationPeriod = 100;
const long displayPeriod = 1000;
int blankValue = 1; //in OD600 units
boolean buttonActive = false;
long operationTime = 2147483647;
double intensity;
float measuredOD;                                                                                       
float calibratedOD;
const long measurementPeriod = displayPeriod; //Over how long of a period to average the output [ms]
const int measurementNumber = (int) (measurementPeriod/integrationPeriod); //Number of measurements to average
int measurements[measurementNumber]; //This stores raw laser measurements
int currentIndex = 0; //Current index used in measument array
unsigned long frq; //square wave pulse count through integration time


void setup() {
  Serial.begin(19200);// connect to the serial port
  pinMode(LEDPin, OUTPUT);
  initDisplayOD();
}

void loop() {
  //If button is not active and it is pressed
  if(!buttonActive && buttonState()){
    Serial.println("Begin blanking mode");
    buttonActive = true;//Set button as active
    operationTime = 0;
    turnOnLED();
    Serial7Segment.print("0000");
  }
  //If button is not pressed
  if(!buttonState()){
    //Serial.println("Button not pressed");
    buttonActive = false;
  }
  //If blanking period just ended
  if(operationTime >= blankingPeriod && operationTime < blankingPeriod + integrationPeriod){
    Serial.println("Ended blanking period");
    //HACK: throws away first 20 blank value while maintaing same display update
    //      and detector reading patter to avoide incorrect blank value due to
    //      information transfer interference
    for (int i=0; i <= 2; i++) {
      Serial7Segment.print("0000");
      for (int k=0; k <= 10; k++) {
        measureOD();
      }
    }
    blankValue = getMeasurement();
    Serial.println(blankValue);
    Serial7Segment.print("    ");
  }

  //If active and not blanking
  if(operationTime < operationPeriod && operationTime >= blankingPeriod && operationTime % displayPeriod < integrationPeriod){
    //Serial.println("Displaying OD");
    displayOD(getOD());
  }
  if(operationTime<operationPeriod){
    measureOD();
  }
  //if operation just ended
  if(operationTime >= operationPeriod && operationTime < operationPeriod + integrationPeriod){
    Serial.println("Shutting down");
    //turn off display
    Serial7Segment.write('v');
    //turn off laser
    turnOffLED();
  }
  if(operationTime < operationPeriod + 2*integrationPeriod) {
    operationTime += integrationPeriod;
  }
}

double getMeasurement() {
  long total = 0;
  for(int i=0; i<measurementNumber; i++){
    total += measurements[i];
  }
  return total*1.0/measurementNumber;
}

double getOD() {
  Serial.println("Getting OD");
  intensity = getMeasurement();
  Serial.println(intensity);
  Serial.println(blankValue);
  measuredOD = -log10(intensity/blankValue);
  //calibration curve
//  calibratedOD = 1.191*measuredOD + 0.02099;
  calibratedOD = 0.9449*measuredOD + 0.005323;
  
  return calibratedOD;
}

void measureOD() {
  if(currentIndex>=measurementNumber){
    currentIndex=0;
  }
  measurements[currentIndex] = readSensor();
  currentIndex++;
}

int readSensor(){
  // Detector must be in pin 5 for arduino uno 
  // wait if any serial is going on
  FreqCounter::f_comp=10;   // Cal Value / Calibrate with professional Freq Counter
  FreqCounter::start(integrationPeriod);  // 100 ms Gate Time

  while (FreqCounter::f_ready == 0)
 
  frq = FreqCounter::f_freq; 
  return frq;
}


void turnOnLED(){
  digitalWrite(LEDPin, HIGH);
}

void turnOffLED(){
  digitalWrite(LEDPin, LOW);
}

void initButton(){
  pinMode(buttonPin, INPUT);
}

boolean buttonState() {
  return digitalRead(buttonPin);
}

void initDisplayOD() {
  Serial7Segment.begin(9600); //Talk to the Serial7Segment at 9600 bps
  Serial7Segment.write('v'); //Reset the display - this forces the cursor to return to the beginning of the display
  Serial7Segment.write(0x7A); // Brightness control
  Serial7Segment.write((byte) 25); // set to 25/255
}

char tempString[100]; //Used for sprintf

void displayOD(double OD) {
  //If Overloaded
  if(abs(OD)>10) {
    Serial7Segment.print("----");
    Serial7Segment.write(0x77);  // Decimal, colon, apostrophe control command
    Serial7Segment.write((byte) 0); // Turns on second decimal
    return;
  }
  if(OD<0) {
    Serial7Segment.print("-");//Print a negative space
  }
  else {
    Serial7Segment.print(" ");//Move cursor forward
  }
  //abs was rounding for some reason
  if(OD<0) {
    OD=-OD;
  }
  sprintf(tempString, "%03d", (int) (OD*100));//Shift the OD two decimal places and then format to the first 3 integers
  Serial.println(tempString);
  Serial7Segment.print(tempString); //Send serial string out the soft serial port to the S7S
  Serial7Segment.write(0x77);  // Decimal, colon, apostrophe control command
  Serial7Segment.write((byte) 2); // Turns on second decimal
}

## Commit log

2015-11-12 Initial solidworks files
    [RODD_v1.1.SLDPRT, RODD_v1.1.STL]
2015-11-18 New verson of RODD casing
    [RODD_v1.2.SLDPRT, RODD_v1.2.STL]
2015-11-19 RODD code now maps ODs to calibration function. Added calibration data folder and files
    [Calibration_Curve.xlsx]
2015-12-02 Resolved blanked value being too high. Added calibration files.
    [Calibration_Curve.xlsx]
2015-12-03 Modified calibration mapping.
    [Calibration_Curve.xlsx]
2015-12-03 Cleaned up repo.
    [Calibration_Curve.xlsx, Casing.SLDPRT, Casing.STL, RODD_v1.1.SLDPRT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]
